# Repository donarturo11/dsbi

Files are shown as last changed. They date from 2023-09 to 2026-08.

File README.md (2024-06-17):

# dsbi
(Damn Simple Brainwave Interface)

This is simple and modular interface for EEG acquisition.
Analog part is brought from [BioAmpExg](https://github.com/upsidedownlabs/BioAmp-EXG-Pill).
The goal of this project is easy assemblation by everyone with very small experience in electronics.
Circuit was tested with ESP32 and AVR Attiny13.

# Data format
Data are sent as raw unsigned 12-bit integer wave with sample rate 512 Hz in following format:
```
unsigned short meteredValue = HHHH HHLL LLLL
unsigned char firstByte  = 10HH HHHH # ( 0x80 | ( (meteredValue >> 6) & 0x3F) )
unsigned char secondByte = 01LL LLLL # ( 0x40 |   (meteredValue & 0x3F) )
```
# Specs
## Common:
* Interface: UART
* Sample rate 512 Hz
* Raw wave 12-bit unsigned short
## ESP32
* Sampling in 12-bit without oversampling
* Hardware UART 8-N-1
* Baudrate: 38400
## Attiny13
* Sampling in 10 bit with oversampling
* Software UART 8-N-2
* Baudrate: 19200
# Compatible software
* [QBrainwaveOSC](https://github.com/donarturo11/QBrainwaveOSC)

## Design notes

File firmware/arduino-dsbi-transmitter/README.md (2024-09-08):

# DSBI transmitter firmware for any Arduino
Just open sketch with ArduinoIDE, build then upload.

## Instructions for Arduino IDE
This sketch was tested on Arduino Uno and Nano, Attiny85 end ESP32 WROOM.
For use with Attiny85, you must to install library ATTinyCore by Spence Konde,
then use for upload dedicated programmer like USBIISP or (if your PC has RS232 port)
use [ponyprog](https://www.lancos.com/siprogsch.html). Very good custom is install bootloader.
I recommend to upload [Optiboot](https://github.com/Optiboot/optiboot) for easy upgrade firmware
without using dedicated programmer, just UART adapter.

# Data format
Data are sent as raw unsigned 12-bit integer wave with sample rate 512 Hz in following format:
```
unsigned short meteredValue = 0bHHHHHHLLLLLL
unsigned char firstByte  = 0b10HHHHHH # ( 0x80 | ( (meteredValue >> 6) & 0x3F) )
unsigned char secondByte = 0b01LLLLLL # ( 0x40 |   (meteredValue & 0x3F) )
```

# Recommended software
Data can be parsed using [QBrainwaveOSC](https://github.com/donarturo11/QBrainwaveOSC).
For using this device, choose baudrate 115200 and Device Type as 2-Byte raw wave parser.

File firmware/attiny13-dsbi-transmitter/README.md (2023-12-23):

# DSBI Transmitter firmware for attiny13
This code is for AVR(R) attiny13.
A simple circuit is in dsbi-transmitter-test.sim1 opened with
[SimulIDE](https://simulide.com/p/).

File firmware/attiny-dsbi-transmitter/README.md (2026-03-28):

# DSBI Transmitter firmware for attiny13/x5
This code is for AVR(R) attiny13/x5. Firmware was tested with
simulide and simulavr.
It samples EEG data with oversampling, and results are sent 512 times in second.
## Simplified schematic
```
                           ____
                   B5/RST |    | VCC
                       B3 |    | PB2         __________
EEG ==> AMPLIFIER ==>  B4 |    | PB1 ==> RX | UART     |
                      GND |____| PB0 <== TX |19200 b/s |
                                            |__________|
```
## Data format
```
data[]={ 0b10HHHHH, 0b01LLLLL }
H - High (MSB)
L - Low (LSB)
```
## Usage
To aqcuire data use [QBrainwaveOSC](https://github.com/donarturo11/QBrainwaveOSC).
The simple circuits for attiny13 and attiny85 are in simulide directory and can be opened with
[SimulIDE](https://simulide.com/p/).
## Simulide
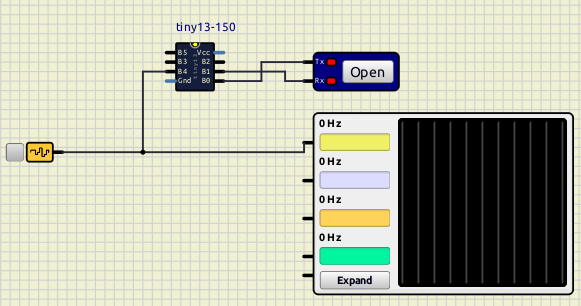
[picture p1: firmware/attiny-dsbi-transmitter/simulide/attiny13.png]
Alt attiny13

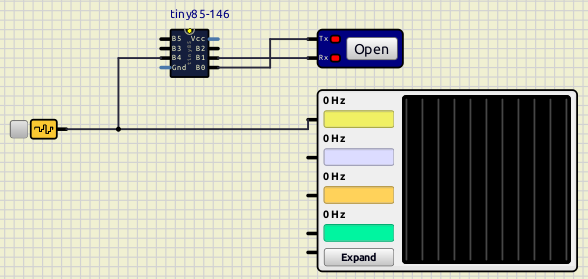
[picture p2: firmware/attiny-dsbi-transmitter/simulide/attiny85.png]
Alt attiny85


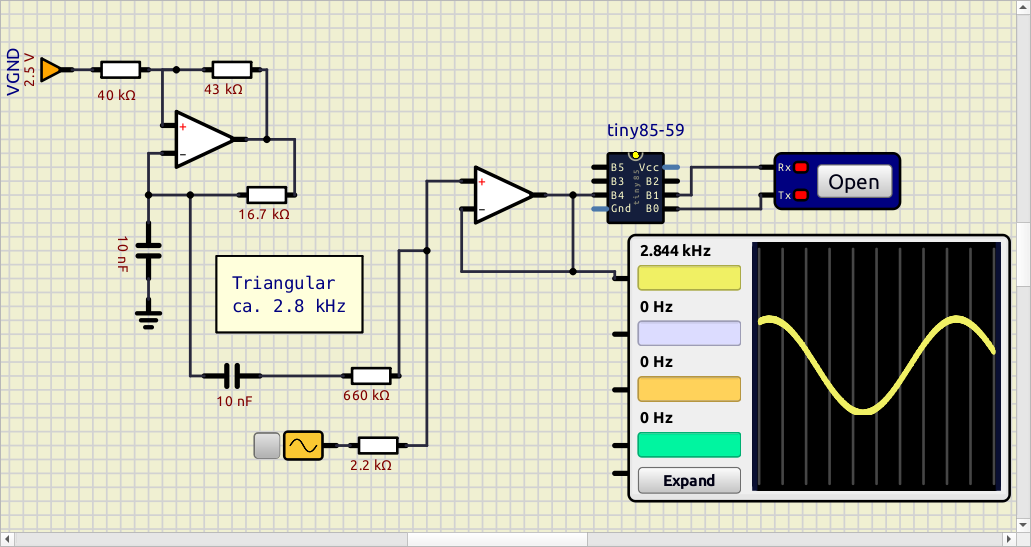
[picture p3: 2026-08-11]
firmware/attiny-dsbi-transmitter/simulide/attiny85_dithering.png

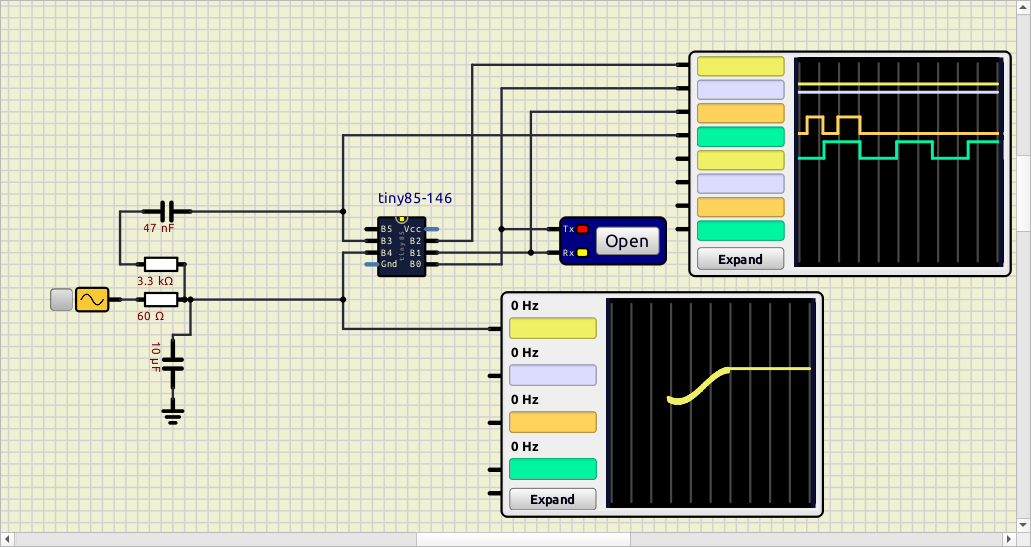
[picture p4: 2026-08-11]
firmware/attiny-dsbi-transmitter/simulide/attiny85_2.png

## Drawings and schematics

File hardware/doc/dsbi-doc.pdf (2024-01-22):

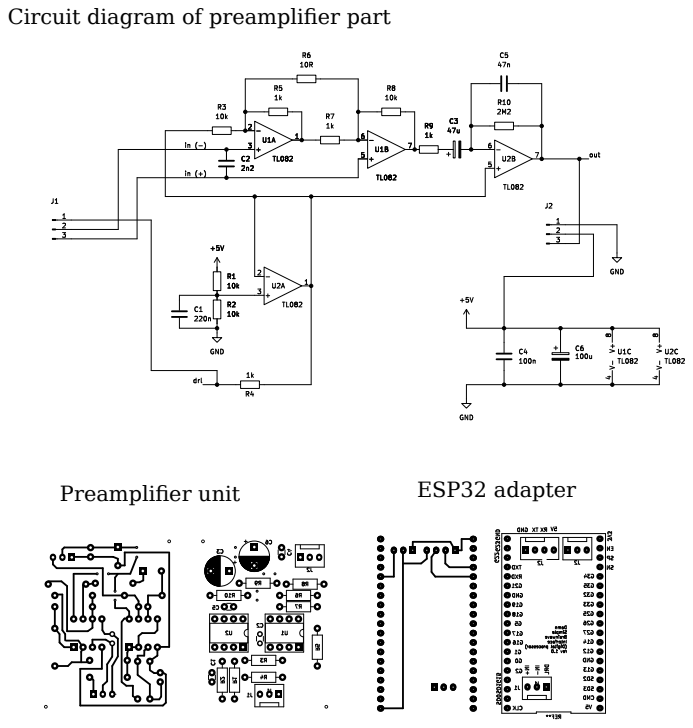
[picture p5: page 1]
Preamplifier unit; ESP32 adapter

Circuit diagram of preamplifier part

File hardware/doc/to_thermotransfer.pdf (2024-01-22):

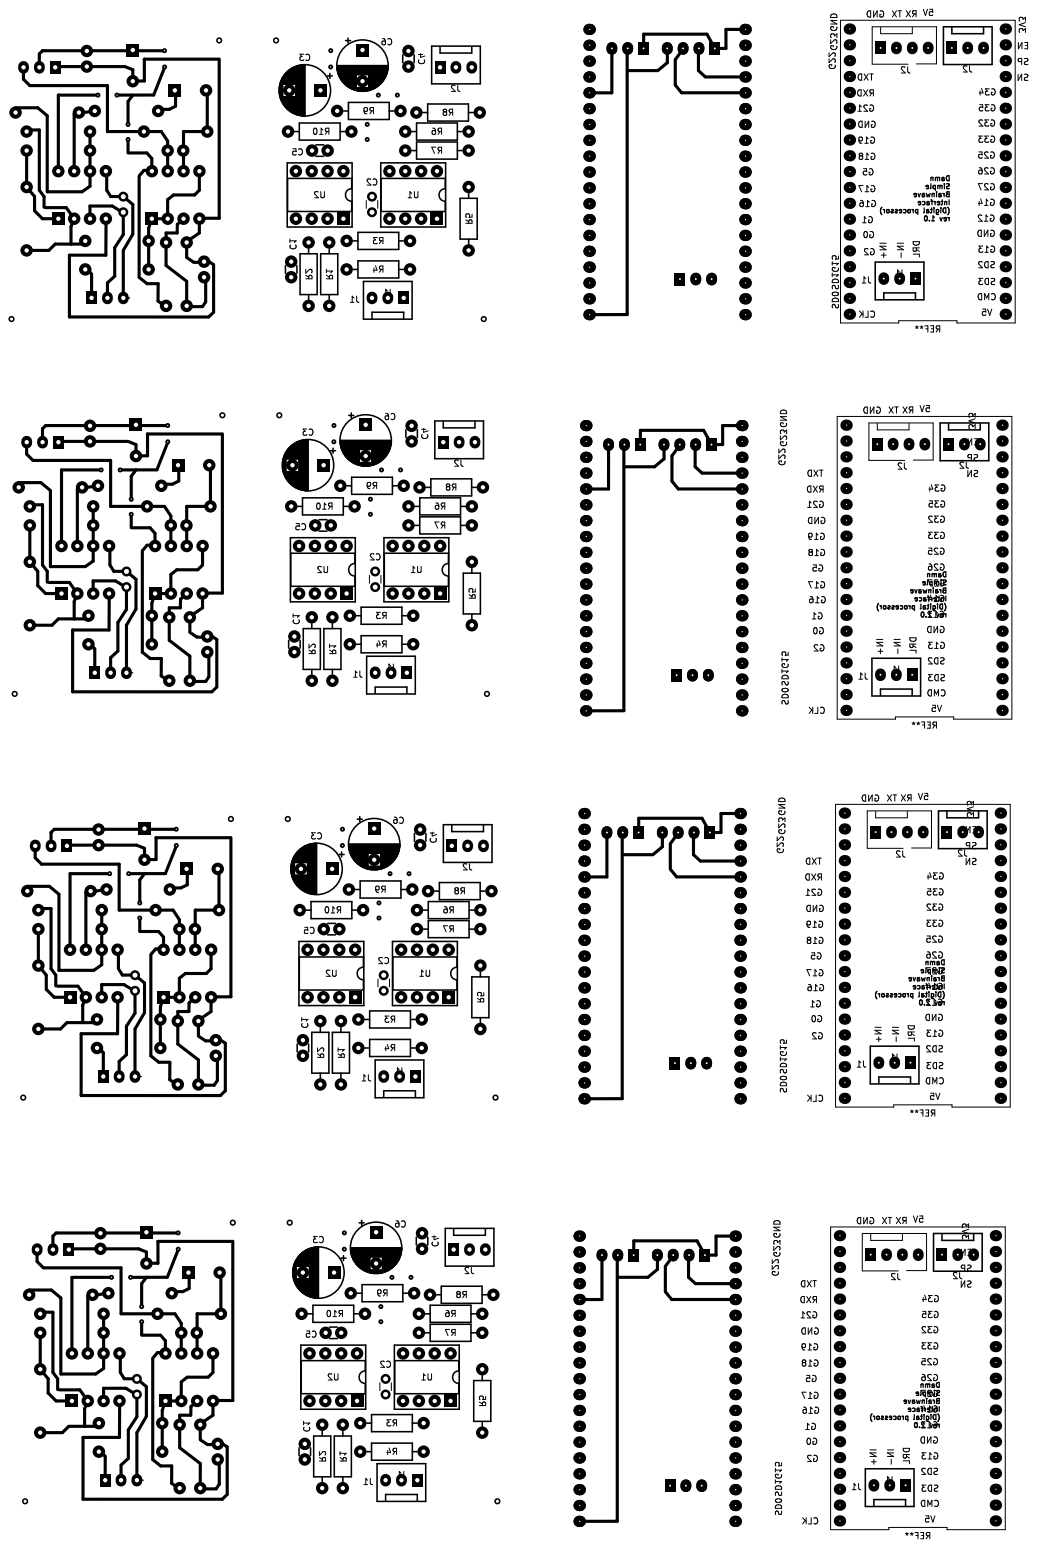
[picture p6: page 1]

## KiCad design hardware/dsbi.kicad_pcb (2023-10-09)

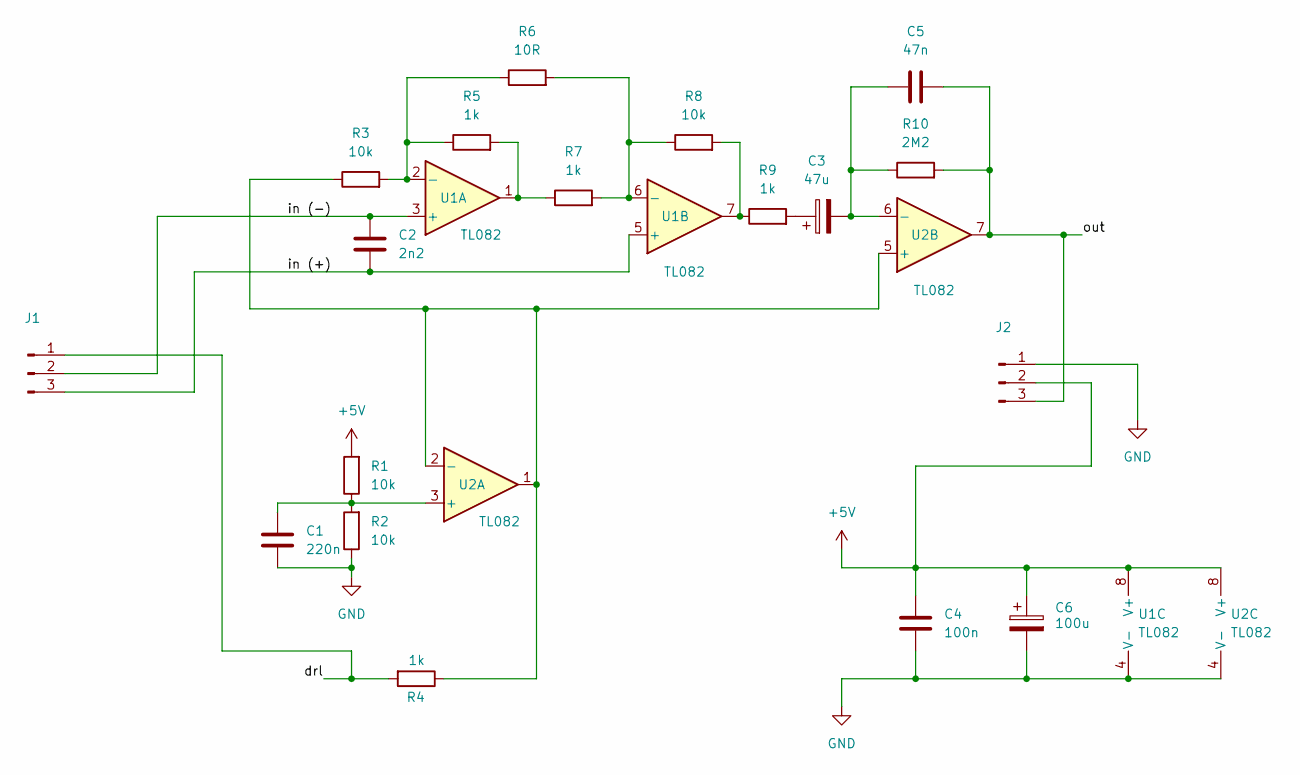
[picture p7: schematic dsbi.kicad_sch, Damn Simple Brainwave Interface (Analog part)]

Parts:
C1: 220n; C_Disc_D3.0mm_W1.6mm_P2.50mm
C2: 2n2; C_Disc_D3.0mm_W1.6mm_P2.50mm
C3: 47u; CP_Radial_D8.0mm_P5.00mm
C4: 100n; C_Disc_D3.0mm_W1.6mm_P2.50mm
C5: 47n; C_Disc_D3.0mm_W1.6mm_P2.50mm
C6: 100u; CP_Radial_D8.0mm_P5.00mm
J1, J2: FanPinHeader_1x03_P2.54mm_Vertical
R1, R2, R3, R8: 10k; R_Axial_DIN0207_L6.3mm_D2.5mm_P10.16mm_Horizontal
R4, R5, R7, R9: 1k; R_Axial_DIN0207_L6.3mm_D2.5mm_P10.16mm_Horizontal
R6: 10R; R_Axial_DIN0207_L6.3mm_D2.5mm_P10.16mm_Horizontal
R10: 2M2; R_Axial_DIN0207_L6.3mm_D2.5mm_P10.16mm_Horizontal
U1, U2: TL082; DIP-8_W7.62mm_Socket

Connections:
+5V: C4.2, C6.1, J2.2, R1.2, U1.8 (V+), U2.8 (V+)
/drl: J1.1, R4.2
/in (+): C2.2, J1.3, U1.5 (+)
/in (-): C2.1, J1.2, U1.3 (+)
/out: C5.2, J2.3, R10.2, U2.7
GND: C1.1, C4.1, C6.2, J2.1, R2.1, U1.4 (V-), U2.4 (V-)
unnamed: C3.1, R9.2
unnamed: R5.2, R7.1, U1.1
unnamed: R8.2, R9.1, U1.7
unnamed: R3.2, R5.1, R6.1, U1.2 (-)
unnamed: R6.2, R7.2, R8.1, U1.6 (-)
unnamed: C1.2, R1.1, R2.2, U2.3 (+)
unnamed: R3.1, R4.1, U2.1, U2.2 (-), U2.5 (+)
unnamed: C3.2, C5.1, R10.1, U2.6 (-)

Board: 2 copper layers, 20 parts (0 on the bottom side), 14 nets, no tracks yet.

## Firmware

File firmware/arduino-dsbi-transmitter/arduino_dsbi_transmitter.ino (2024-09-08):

/*
*
*   Donarturo11 - Damn Simple Brainwave Interface
*   Firmware to send brainwaves data values to computer
*   https://github.com/donarturo11/dsbi
*
*   
*   
*/

#if defined(__AVR_ATtiny85__)
#define ANALOGPIN 1
#define BAUD 115200
#define ADC_RESOLUTION 10
#elif defined(ESP32)
#define ANALOGPIN 34
#define BAUD 115200
#define ADC_RESOLUTION 12
#else
#define ANALOGPIN A0
#define BAUD 115200
#define ADC_RESOLUTION 10
#endif

#define SAMPLE_RATE 512
#define SAMPLE_DELAY 1000000 / SAMPLE_RATE

unsigned short sample = 0;

void setup() {
  Serial.begin(BAUD);
  #ifdef AREF_MODE
  analogReference(AREF_MODE);
  #endif
}

void loop() {
  uint8_t msb_byte = 0x80;
  uint8_t lsb_byte = 0x40;  
  #if ADC_RESOLUTION == 10
  unsigned int adcTotal = 0;
  for (char i=0; i<16; i++) {
      adcTotal += analogRead(ANALOGPIN);
  }
  adcTotal = (adcTotal >> 2);
  sample = (adcTotal)&0xFFFF;
  #elif ADC_RESOLUTION == 12
  sample = analogRead(ANALOGPIN);
  #endif
  msb_byte |= (sample >> 6) & 0x3F;
  lsb_byte |= sample & 0x3F;
  Serial.write( msb_byte );
  Serial.write( lsb_byte );
  delayMicroseconds(SAMPLE_DELAY);
}

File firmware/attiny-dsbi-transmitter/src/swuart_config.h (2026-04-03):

/* vim: set sts=4 sw=4 et: */

#ifndef SWUART_CONFIG_H
#define SWUART_CONFIG_H

#include "global.h"

#ifdef TXPIN
#define TXMASK (1<<TXPIN)
#endif
#ifdef RXPIN
#define RXMASK (1<<RXPIN)
#endif

#define STOP_BITS 2

#define BIT_CYCLES (F_CPU/BAUD_RATE)
#define BAUD_DELAY ((uint8_t)((BIT_CYCLES/TIMER_PRESCALER)-1))

#endif

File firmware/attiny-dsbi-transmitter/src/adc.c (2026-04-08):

/* vim: set sts=4 sw=4 et: */

#include <avr/io.h>
#include <avr/interrupt.h>
#include "global.h"
#include "adc.h"

volatile data_handler_t ADC_handler;
static void ADC_nop(void* data) {
    void *d = data;
    asm("nop");
}

void ADC_init() {
    ADC_cnt=OVERSAMPLE_COUNT;
    ADC_acc = 0;
    ADC_result = 0;
    
    ADMUX|=(1<<MUX1);
    ADCSRA=(1<<ADEN)|(1<<ADIE);
    ADCSRA|=(1<<ADPS2)|(0<<ADPS1)|(1<<ADPS0);
    ADC_handler.fn=ADC_nop;
    ADC_handler.data=0;
}

void ADC_begin()
{
    OCR0A = SAMPLE_DELAY;
    TIMSK|=(1<<OCIE0A);
    timer0A_isr = ADC__timer_isr;
}

void ADC_end()
{
    OCR0A = 0;
    TIMSK&=~(1<<OCIE0A);
    timer0A_isr = 0;
}

void ADC_poll()
{
    if (ADC_cnt & 0x80) {
        ADC__on_oversampling_ready();
    }
}

void ADC__on_oversampling_ready() {
    uint16_t result;
    ADC_cnt &= 0x7F;
    ADC_result >>= DECIMATION_COUNT;
    ADC_result /= ADC_AVERAGING;
    result = (uint16_t) ADC_result;
    ADC_result = 0;
    ADC_handler.data=&result;
    if (ADC_handler.fn)
      ADC_handler.fn(ADC_handler.data);
}


void ADC__on_sampling_ready() {
    if (ADC_cnt--) {
        ADC_acc += (uint32_t) ADC;
    }
    if (!ADC_cnt) {
        ADC_result = ADC_acc;
        ADC_cnt=OVERSAMPLE_COUNT | 0x80;
        ADC_acc=0;
    }
}

void ADC__timer_isr() {
    ADCSRA|=(1<<ADSC);
    asm ("ldi r23,%[delay]\n\t"
         "add r24,r23\n\t"
         ::[delay] "i" (SAMPLE_DELAY));
}

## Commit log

2023-09-17 Add KiCad project
    [dsbi.kicad_pcb, dsbi.kicad_sch]
2023-09-17 Add code for ESP32
2023-09-20 Initial create circuits (#1)
    * Arrangement of elements
    * paths
    * Do not track production files
    * Most paths
    * Rearrange elements
    * Create new PCB paths
    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
    [dsbi-digital-part.kicad_pcb, dsbi.kicad_pcb]
2023-09-22 fix details
    [dsbi.kicad_pcb]
2023-09-22 Move text from back cu to front silkscreen
    [dsbi.kicad_pcb]
2023-10-09 Connect TL072 ICs to GND
    [dsbi.kicad_pcb]
2023-10-09 Resize holes
    [dsbi.kicad_pcb]
2023-10-09 Resize holes #2
    [dsbi.kicad_pcb]
2023-10-09 Increase path distances
    [dsbi.kicad_pcb]
2023-12-23 Move code for ESP32 to another directory
2023-12-23 Add README for ESP32 firmware
2023-12-28 Prepare circuit for test samplerate
2024-01-22 Add PDFs for easily printing
2024-04-10 Change ESP32 firmware to unsigned 2-byte raw wave
2024-07-25 Rename sketch file for ESP32
2024-07-25 Add sketch for Arduino
2024-09-08 Add more instructions for another microcontrollers for use in Arduino IDE
2024-09-08 Remove unnecessary sketch because using universal one for Arduino
